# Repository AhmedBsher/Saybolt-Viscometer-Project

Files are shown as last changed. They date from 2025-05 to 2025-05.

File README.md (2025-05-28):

# Saybolt Viscometer Project

**Ahmed M. Bsher**<br>
ahmedbsher999@gmail.com<br>
**Alexandria University – Faculty of Engineering** – Mechanical Engineering

---

## Project Overview

This project is a Semi-Automated Saybolt Viscometer designed to measure the kinematic viscosity of Newtonian fluids. It combines mechanical design, sensor technology, microcontroller programming, and data analysis to provide a low-cost, modern alternative to traditional viscometers.

The viscometer measures the time taken for a fixed volume (60 ml) of fluid to flow through a standard orifice. This flow time is then used to calculate the fluid's viscosity using calibrated equations.

---

## Key Features

-   **Semi-Automated Measurement:** Uses an ESP32 microcontroller and an HC-SR04 ultrasonic sensor to automate fluid level measurement and time calculation.
-   **Real-Time Display:** LCD screen provides live viscosity readings.
-   **Dual Calibration:** Separate equations for fast-flowing and slow-flowing fluids to ensure accuracy.
-   **Python GUI Calculator:** A Tkinter-based application for easy viscosity calculation.
-   **Uncertainty Analysis:** Detailed MATLAB-based analysis to evaluate measurement accuracy and error sources.
-   **SolidWorks Design:** Precisely designed mechanical enclosure using SolidWorks23.

---

## Technologies and Tools Used

-   **ESP32 Microcontroller:** Main control unit for sensor data processing and output.
-   **HC-SR04 Ultrasonic Sensor:** For measuring fluid levels in the beaker.
-   **16x2 LCD Screen:** To display real-time viscosity readings.
-   **SolidWorks23:** For designing the mechanical enclosure.
-   **Python (Tkinter):** For developing the viscosity calculation GUI.
-   **MATLAB:** For uncertainty analysis.

---

## Project Components

### Mechanical Design

-   Designed in SolidWorks23 with a rectangular box enclosure, LCD screen cutout, and funnel opening.
-   Tab-and-slot construction for easy assembly and stability.
-   Internal support columns for the ultrasonic sensor.

### Sensor and Control System

-   HC-SR04 ultrasonic sensor for fluid level measurement.
-   ESP32 microcontroller for processing sensor data and displaying results.
-   16x2 LCD screen for displaying viscosity readings.

### Software

-   **ESP32 Firmware:** Code to read sensor data, calculate flow time, and display viscosity.
-   **Python GUI (`viscosity_calculation_gui.py`):**
    -   Tkinter application for viscosity calculation based on input time.
    -   Separate calibration equations for fast and slow flows.
-   **MATLAB Scripts:** For uncertainty analysis and error quantification.

---

## Calibration

-   Two sets of calibration equations:
    -   Fast-flowing fluids (water, milk): `v = 0.2447656223 * t - (0.06153034765 / t)`
    -   Slow-flowing fluids (oil): `v = 1.297738228 * t - (-235.6160549 / t)`
-   Calibration constants derived from tests with reference fluids.

---

## Uncertainty Analysis

-   Conducted using MATLAB to evaluate measurement accuracy.
-   Identified sources of uncertainty:
    -   Sensor resolution
    -   Wave reflection
    -   Power supply fluctuations
    -   Fluid properties
    -   Temperature errors
-   Calculated combined and expanded uncertainties to provide a confidence interval.

<p align="center">
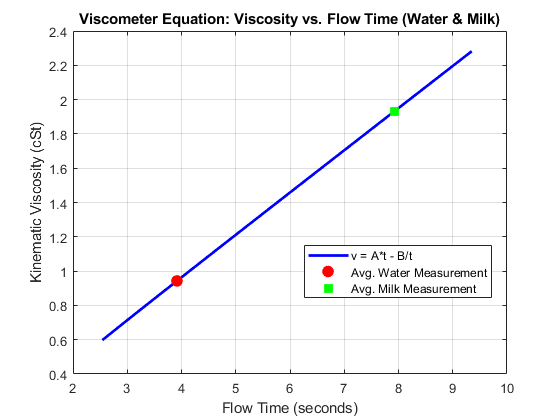
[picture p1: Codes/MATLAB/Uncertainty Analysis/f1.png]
  
</p>

<p align="center">
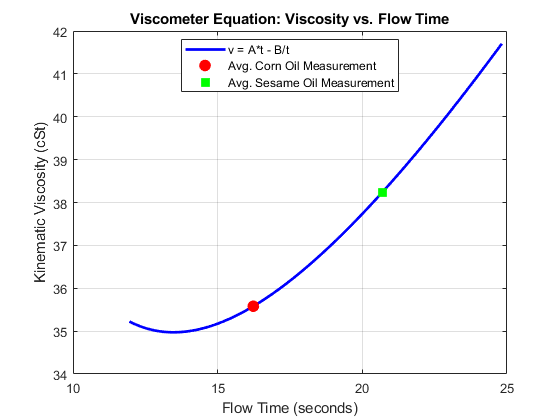
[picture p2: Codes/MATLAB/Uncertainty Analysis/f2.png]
  
</p>

---

## Getting Started

1.  Clone the repository to your local machine.
2.  Review the `SAYBOLT Viscometer Project Report.pdf` for detailed information.
3.  Explore the `Codes` folder for the Python GUI.
4.  Check the `Software` folder for the ESP32 firmware.
5.  Refer to the `Gallery` for project images.

### Running the Python GUI

1.  Ensure Python and Tkinter are installed.
2.  Navigate to the `Software` folder.
3.  Run `python viscosity_calculation_gui.py`.

---

## Contact

**Ahmed M. Bsher**<br>
ahmedbsher999@gmail.com<br>
[LinkedIn](https://www.linkedin.com/in/ahmed-bsher-921242232/)<br>
[Portfolio Website](https://ahmedbsher.github.io/My-Portfolio/)

---

## Tags

`#Engineering` `#Electronics` `#EmbeddedSystems` `#Viscosity` `#SayboltViscometer` `#ESP32` `#Arduino` `#Python` `#Tkinter` `#SolidWorks` `#Sensors` `#Measurement` `#FluidMechanics` `#Project`

---

## License

This project is licensed under the MIT License.

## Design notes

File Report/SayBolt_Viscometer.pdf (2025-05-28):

# Contents

3

# 1.Introduction:

Viscosity is one of the most important physical properties of fluids,

as it represents the internal resistance to flow. engineers must measure viscosity

Because it’s needed in many applications, such as lubrication systems, pipeline

design, chemical processing, and quality control. Our device is a classical

device that is used for determination of Newtonian fluids' kinematic viscosity

and its name Saybolt Viscometer

The working principle is simple measures the time it takes for a fixed volume

(typically 60 ml) of fluid to flow through a standard orifice at a specified

temperature

This project aims to simulate this process with a low-cost, Semi-automated

alternative using modern sensors and microcontrollers.

that provides live measurements and calculates viscosity with reasonable

accuracy.

The main objective is to design and construct an Semi-automated

## “Saybolt Viscometer”

4

# 2.Design and Methodology:

### 2.1 Mechanical Design

- Components
- Funnel
- Beaker
- Box
- 2 Wooden bars
- Box design

The outer box was designed with Solidworks23. A Rectangular cut-out

was included on the front panel for the LCD screen to allow clear

visibility of the readings. Additionally, an opening was made at the top to

securely insert the funnel used for fluid filling. The entire box was

assembled using a tab-and-slot construction method, ensuring ease of

assembly, precise alignment, and mechanical stability. Inside the box, the

ultrasonic sensor was fixed in place using two horizontal support

columns. These columns ensured that the sensor remained stable and

accurately aligned above the beaker for consistent distance

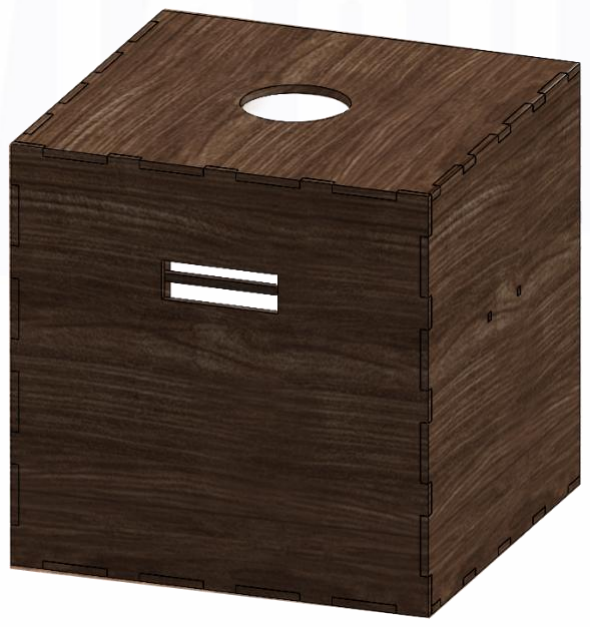
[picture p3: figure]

measurements.

5

### 2.2Sensor and Control System:

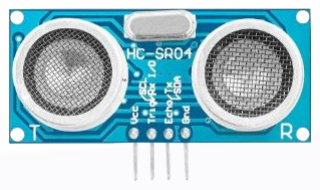
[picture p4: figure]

- HC-SR04 ultrasonic sensor

The sensor sits right atop the beaker
To measure the distance that is between the sensor and the rising
liquid level.
- ESP32 microcontroller

The ESP32 microcontroller is used as the main control unit in the Saybolt Viscometer project. It is responsible for receiving data from sensors, processing the information, and displaying the results.

- LCD

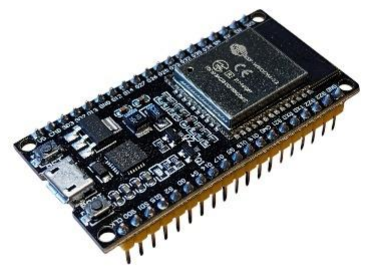
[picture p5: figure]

The screen is interfaced using multiple digital pins for direct control over each function (such as RS, EN, D4–D7), rather
than using a simplified I2C communication

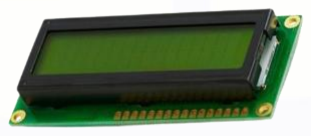
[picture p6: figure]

### 2.3 Operational Workflow

1. Fluid is poured into a funnel.

### 2. A beaker is placed under the funnel

### 3. Sensor measures the height of fluid

### 4. Height change is used to calculate time

### 5. Time for 60 ml to flow is calculated

### 6. Time is then used to calculate viscosity

6

## 3. Calibration:

Equation Format:

The standard empirical equation is:

## ν = A · t − (

B
t

)

Where :

- ν : Kinematic viscosity (mm²/s or cSt)
- t : Flow time in seconds
- A,B : Constants to be determined by calibration

We made two calibrated equations, one for fast-flowing fluids and the other for slow-flowing fluids

3.1: calibrating the equation for fast-flowing fluids

We used two equations for two different reference fluids to calculate the constants in Saybolt equation

1.Reference fluids:
1) Water:
properties:
- v water = 0.89 mm²
/s
- Volume used = 60 ml
- Measured discharge times (seconds): [3.32, 4.39, 3.32, 4.28, 3.21]
- Average time :
taveragefor water = (3.32 + 4.39 + 3.32 + 4.28 + 3.21) / 5 = 3.704 s
2) Milk:
properties:
- v milk = 1.8 mm²
/s
- Volume used = 60 ml
- Measured discharge times (seconds): [7.6, 7.39, 6.64, 7.49, 7.82]
- Average time :
taverge for milk =

7.6+7.39+6.64+7.49+7.82

5

= 7.388 s

7

2.Substituting into the Equation :

1) For water ∶ 0.89 = A ∗ 3.704 − (

B
3.704)
2) For milk ∶ 1.8 = A ∗ 7.388 – (

B
7.388)

∗ Solving the two equations and we get A, B ∗

A = 0.2447656223

B = 0.06153034765

3.Final calibrated equation for fast-flowing fluids :

v | = | 0.2447656223 | ∗ | t – | (

0.06153034765
t

)

3.2: calibrating the equation for slow-flowing fluids

We did the same process in oil.
1) Substituting into the Equation :
Solving the two equations and we get A,B

A = 1.297738228

B = −235.6160549

3.Final calibrated equation for slow-flowing fluids :

v | = | 1.297738228 | ∗ | t – (

−235.6160549
t

)

8

# 4. Testing and Results:

Results for Fast-Flowing Fluids

Fluid | Time (s) | Viscosity (mm²/s)
Water | 3.73 | 0.896
Water | 4.28 | 1.033
Water | 4.28 | 1.033
Water | 3.75 | 0.901
Water | 3.54 | 0.849
Milk | 8.35 | 2.036
Milk | 8.03 | 1.958
Milk | 7.7 | 1.877
Milk | 7.28 | 1.773
Milk | 8.24 | 2.009

Accuracy for water readings = 94.08 %

Accuracy for milk readings = 92.74 %

Results for Slow-Flowing Fluids

Fluid | Time (s) | Viscosity (mm²/s)
Oil | 13.95 | 34.993
Oil | 14.13 | 35.012
Oil | 18.94 | 37.019
Oil | 16.8 | 35.827
Oil | 17.34 | 36.091
Accuracy for Oil readings = 97.75 %

9

# 5.Uncertainty Analysis:

An uncertainty analysis was conducted to evaluate the accuracy of the viscosity measurements and identify potential sources of error.

### 5.1 Sources of Uncertainty

Several sources of uncertainty were identified based on the experimental setup and device characteristics:
- Sensor Resolution: The HC-SR04 sensor has a resolution of 0.3 cm, limited by the speed of sound and timing accuracy. Small changes in fluid level below this resolution may lead to unstable measurements. Additionally, variations in air density or humidity affect the speed of sound, introducing further errors.
- Wave Reflection: The fluid surface (e.g., oil or water) may reflect ultrasonic waves unevenly due to turbulence or transparency, weakening the signal and reducing measurement reliability, especially for highly reflective fluids.
- Power Supply: The ESP32 supplies the HC-SR04 with 5V via USB or another source. Voltage fluctuations can affect sensor performance, leading to inaccurate measurements.
- Viscometer Factors: Impurities or non-uniformity in the fluid composition may affect flow time, causing variability in viscosity measurements. Mechanical vibrations or instability in the setup can also impact sensor stability.
- Temperature Errors: Fluid temperature deviations cause a 1–2% error in viscosity per degree Celsius, while environmental temperature affects the HC-SR04 by approximately 0.17% per degree Celsius. This can result in a cumulative error of 2,5% in flow time if conditions are not controlled.

10

### 5.2 Uncertainty Calculation

### Theoretical Basis

- The kinematic viscosity (v) is calculated using the standard Saybolt Viscometer Equation, which describes the relationship between the flow time of a fluid through a calibrated orifice and its viscous properties:

## v = A ∗ t −

B
t
- A and B are the calibration constants specific to the viscometer used. For the purpose of this analysis, the uncertainty in these constants is assumed to be negligible.

1-Calculation of the Sensitivity Coefficient (dv/dt): This coefficient indicates how much the viscosity changes with a change in flow time. It's calculated by taking the derivative of the viscosity equation with respect to time:

2-Calculation of the Standard Uncertainty of the Mean Flow Time (ut ): This uncertainty is estimated from the observed variability in repeated flow time measurements. If we have n flow time measurements, the standard uncertainty of the mean time is calculated from the standard deviation

3-Assumption for Temperature Uncertainty (u_v _temperature)=0

4-Calculation of the Combined Standard Uncertainty (uc _(v)): To combine the individual uncertainty contributions from all relevant sources into a single overall value, the Law of Propagation of Uncertainty is applied.

dv
dt

= A +

B
T

2

Ut =

### std_dev(t)

√n

## uc _(v) = √(

dv
dt

∗ Ut)

## 2 + u_v _temperature²

11

## U = K ∗ uc _(v)

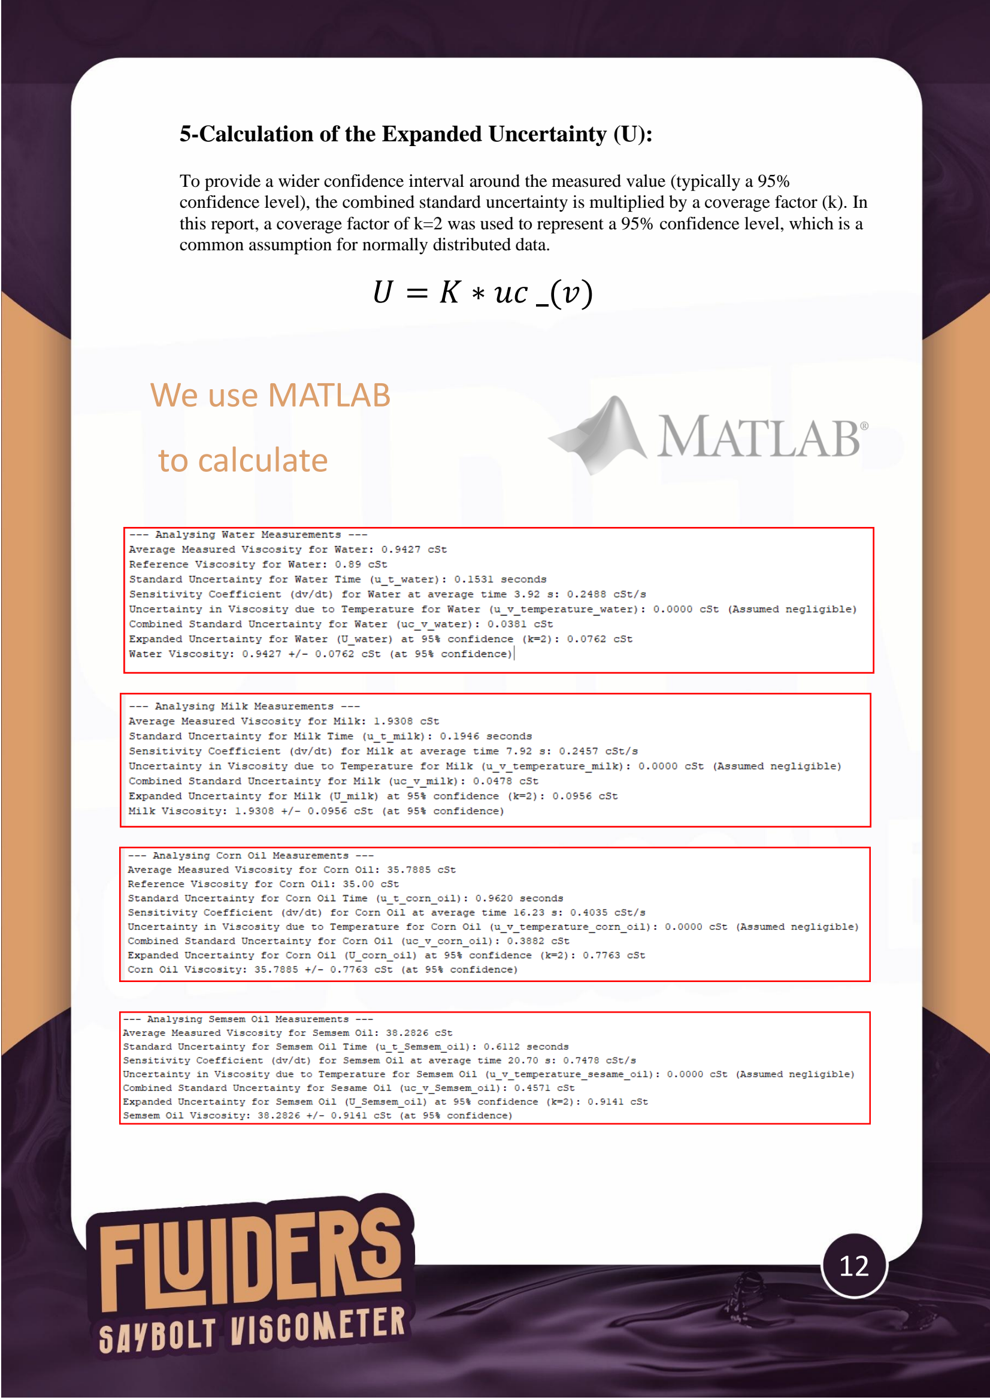
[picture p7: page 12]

5-Calculation of the Expanded Uncertainty (U):

To provide a wider confidence interval around the measured value (typically a 95% confidence level), the combined standard uncertainty is multiplied by a coverage factor (k). In this report, a coverage factor of k=2 was used to represent a 95% confidence level, which is a common assumption for normally distributed data.

# We use MATLAB

# to calculate

12

# 6.Discussion

6.1 Strengths of the Design:

- Low Cost: Utilizes affordable components accessible to students and hobbyists.
- Automation: The process is fully automated, eliminating the need for manual timing and control.
- Live Feedback: Real-time readings are displayed on the LCD screen, enhancing usability.
- Hands-On Learning: The project provided valuable experience in coding, circuit design, and hardware troubleshooting.
- Redesign Success: After an initial failure, we successfully created a functional design that fits all components properly.
6.2 Limitations:
- Ultrasonic Sensor Sensitivity: Highly affected by environmental noise, leading to unstable readings unless properly isolated.
- Initial Design Flaws: The first prototype did not accommodate the board and components effectively.
- Connection Issues: Wiring and circuit stability required extra effort and learning through trial and error.
- Lack of Temperature Control: Saybolt standards require 40°C or 100°C testing, while our setup operates at room temperature.
- Mathematical Complexity: Calculations required for viscosity were initially difficult to apply correctly.

6.3 Future Improvements:

- Replace ultrasonic sensor with a more stable alternative or apply digital signal filtering.
- Incorporate temperature sensors (e.g., DS18B20) to comply with Saybolt standard conditions.
- Modular Hardware Design: Easier troubleshooting and component swapping.
- Enhance coding structure for scalability and easier debugging.
- Add data logging capability via SD card or Bluetooth module for record keeping.

13

6.4 Cost:

- ESP : 320EGP
- HC-SR04 ultrasonic sensor : 45EGP
- Character LCD 16*2 Display Module : 70 EGP
- Jumpers : 45 EGP
- Design : 280 EGP
- Resistors : 5 EGP
- Metal Potentiometer : 5.50 EGP
- Breadboard : 40 EGP
- Cone : 25 EGP
- Beaker : 40 EGP
Total cost = 875.5 EGP

# 7.Conclusion

In conclusion, the Saybolt viscometer combined with an HC-SR04 ultrasonic sensor, ESP32 microcontroller introduces a novel low-cost digital method of measuring viscosity using digital accuracy for automatic data collection. Its accuracy is limited by uncertainties related to environmental influences on ultrasonic wave propagation, sensor resolution, microcontroller timing jitter, and fluid property or tube geometry variation. Using temperature compensation, careful calibration, stable power supplies, and sensor alignment, all these uncertainties can be reduced, making the system more reliable.

14

## 8. Project Gallery

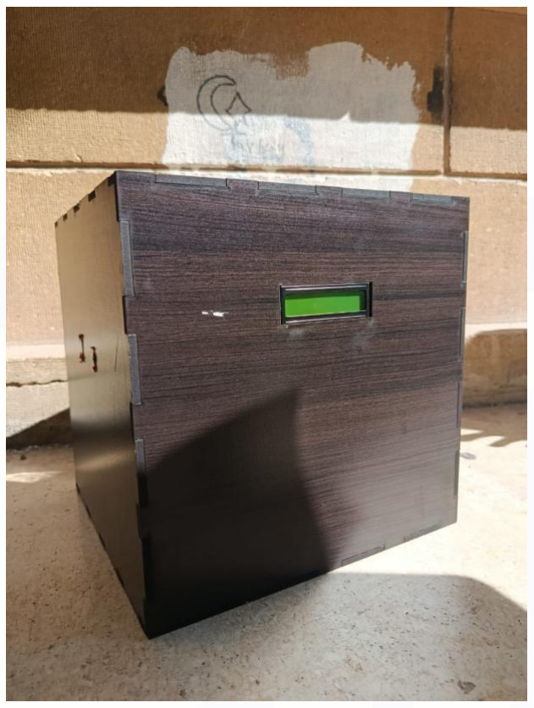
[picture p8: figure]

# 9. References:

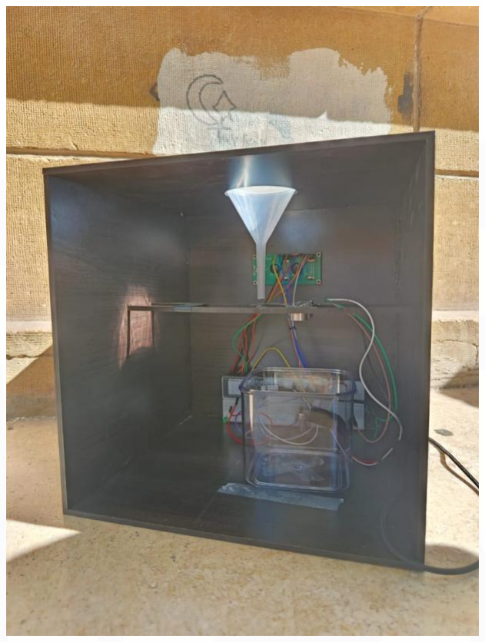
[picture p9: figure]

- https://instrumentationtools.com/saybolt-viscometer/
- https://www.slideshare.net/slideshow/saybolt-viscosity/125332774
- https://www.scribd.com/document/170513997/Say-Bolt-viscometer
- https://nvlpubs.nist.gov/nistpubs/nbstechnologic/nbstechnologicpaperT112e1.pdf
- ASTM International, Standard Test Method for Saybolt Viscosity, ASTM D88, 2018.Available: https://www.astm.org/d0088-18.html
- D. W. Green and M. Z. Southard, Perry’s Chemical Engineers’ Handbook, 9th ed. NewYork: McGraw-Hill Education, 2019, ch. 2.
- R. Santos and S. Araujo, “Using the HC-SR04 Ultrasonic Sensor with the ESP32,”Random Nerd Tutorials, 2021. [Online]. Available: https://randomnerdtutorials.com/esp32-hc-sr04-ultrasonic-arduino/
- Malarvizhi and R. Sudha, “Ultrasonic Measurement of Liquid Level,” International Journal of Engineering Research & Technology (IJERT), vol. 6, no. 8, pp. 1–4, Aug. 2017.
- A Beginner's Guide to Uncertainty of Measurement

15

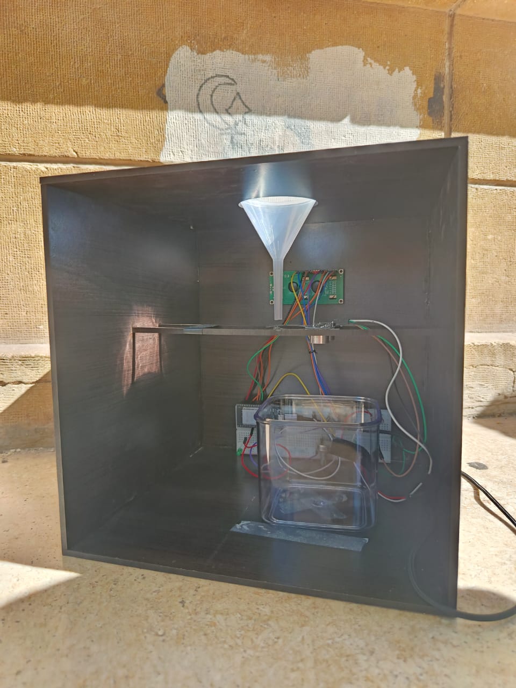
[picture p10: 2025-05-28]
Gallery/back.jpg

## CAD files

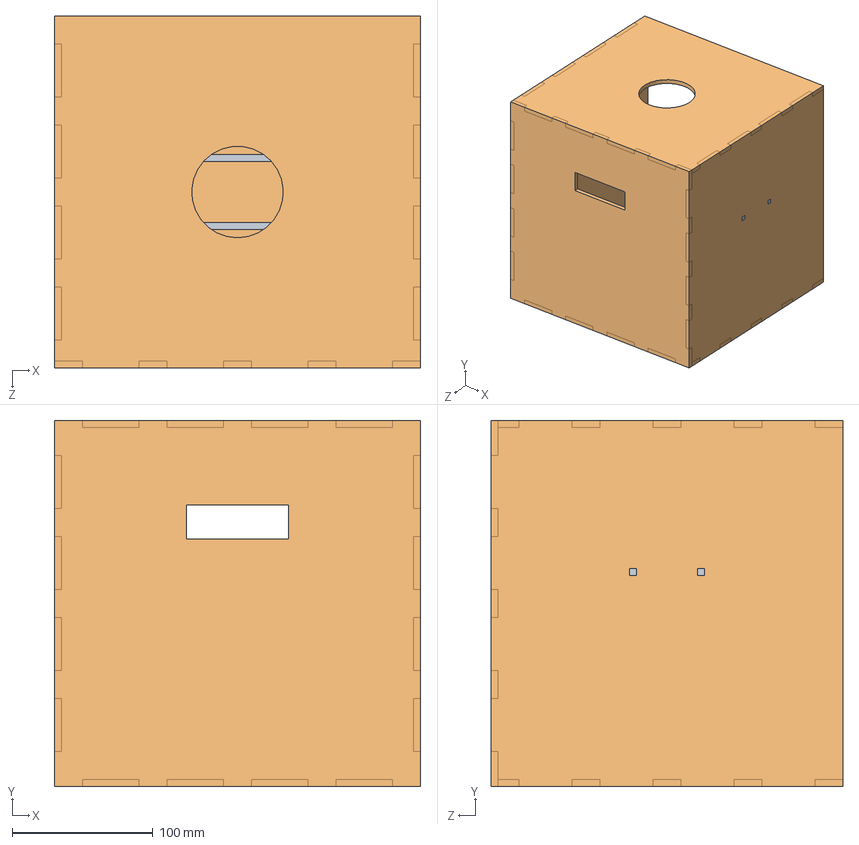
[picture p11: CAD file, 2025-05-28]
Design/Assem2.SLDASM
260.0 x 260.0 x 250.0 mm
arm x 2

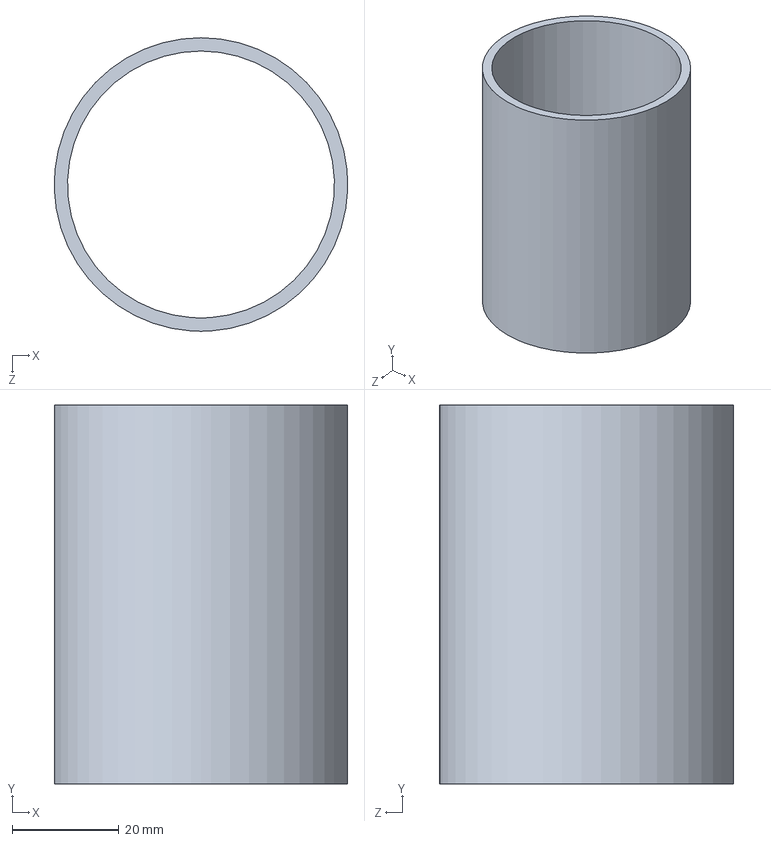
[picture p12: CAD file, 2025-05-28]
Design/baker.SLDPRT
55.0 x 71.0 x 55.0 mm

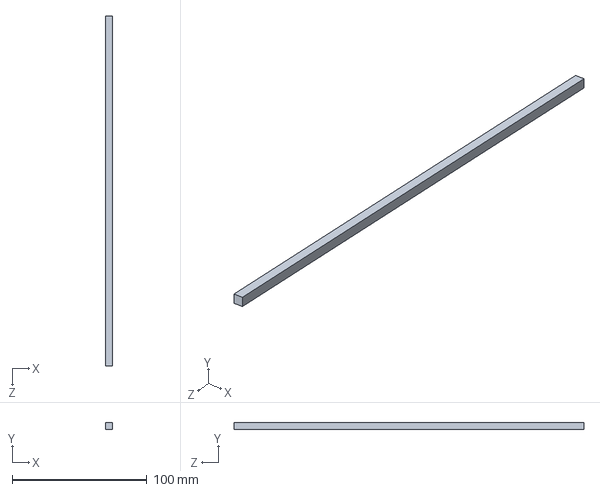
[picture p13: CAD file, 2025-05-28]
Design/arm.SLDPRT
5.00 x 5.00 x 260.0 mm

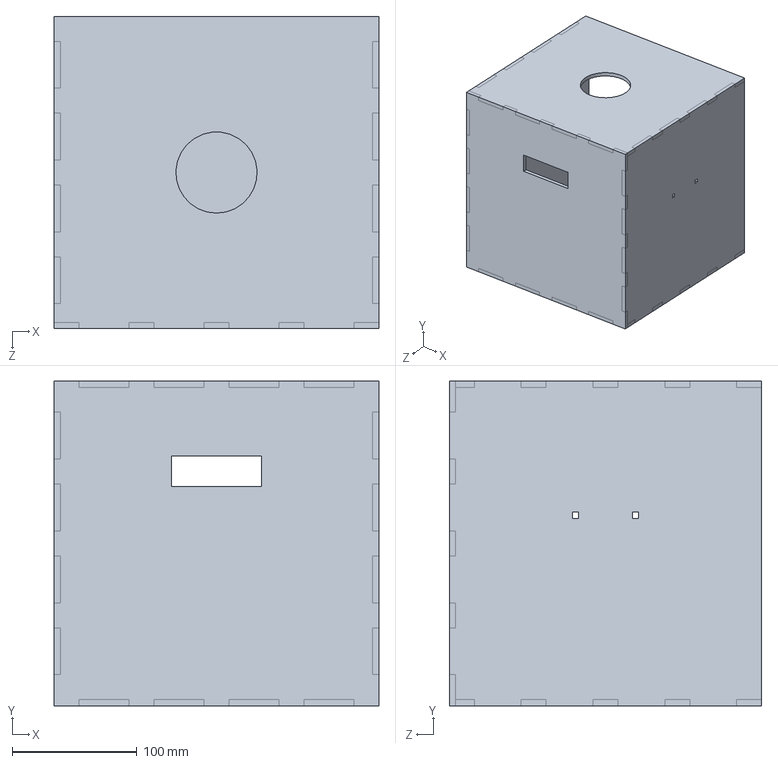
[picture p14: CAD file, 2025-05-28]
Design/box.SLDPRT
260.0 x 260.0 x 250.0 mm

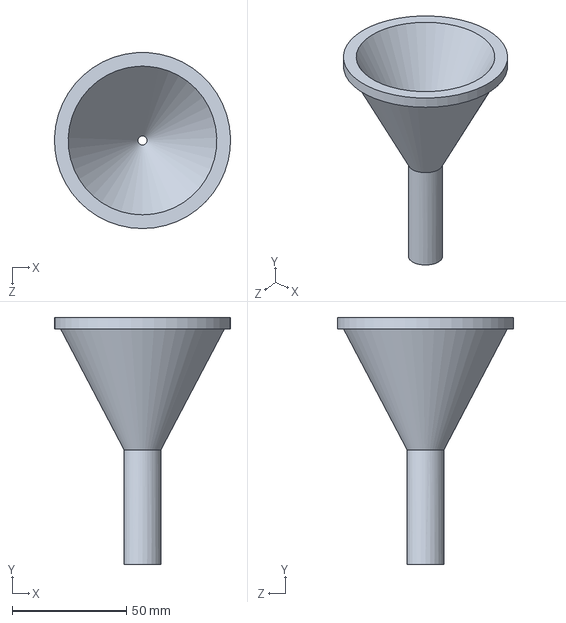
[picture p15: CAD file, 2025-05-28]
Design/cone.SLDPRT
77.0 x 108.0 x 77.0 mm

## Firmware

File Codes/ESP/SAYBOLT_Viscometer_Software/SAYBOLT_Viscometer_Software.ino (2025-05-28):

#include <LiquidCrystal.h>

// LCD pins: RS, E, D4, D5, D6, D7
LiquidCrystal lcd(21, 22, 18, 19, 23, 5);

// Ultrasonic sensor pins
#define TRIG_PIN 4
#define ECHO_PIN 16
#define LED_PIN 32

// Measurement parameters
const float SOUND_SPEED = 0.034; // cm/μs
const float MIN_DISTANCE = 10.00;  // cm
const float MAX_DISTANCE = 15.00;  // cm

#define MEDIAN_FILTER_SIZE 5
float distanceBuffer[MEDIAN_FILTER_SIZE];
byte bufferIndex = 0;
const float SMOOTHING_FACTOR = 0.7;
float smoothedDistance = 0;
float lastValidDistance = 0;

const int DEBOUNCE_COUNT = 3;
int debounceCounter = 0;
unsigned long startTime = 0;
unsigned long stopTime = 0;
bool timing = false;
bool finished = false;
bool gracePeriod = true;
unsigned long graceStartTime = 0;
const unsigned long GRACE_PERIOD = 10000;

const float D1 = 13.84;
const float D2 = 11.835;

const float A_FAST = 0.2447656223;
const float B_FAST = 0.06153034765;
const float A_SLOW = 1.297738228;
const float B_SLOW = -235.6160549;
const float TIME_THRESHOLD = 10.0;

void setup() {
  Serial.begin(115200);
  pinMode(TRIG_PIN, OUTPUT);
  pinMode(ECHO_PIN, INPUT);
  pinMode(LED_PIN, OUTPUT);

  lcd.begin(16, 2);
  lcd.print("Initializing...");

  for (byte i = 0; i < MEDIAN_FILTER_SIZE; i++) {
    distanceBuffer[i] = getRawDistance();
    delay(50);
  }

  lastValidDistance = medianOfArray(distanceBuffer, MEDIAN_FILTER_SIZE);
  smoothedDistance = lastValidDistance;

  graceStartTime = millis();
  updateDisplay();
  Serial.println("System Ready - Enhanced Stability Active");
}

void loop() {
  if (finished) {
    delay(1000);
    return;
  }

  float currentDistance = getFilteredDistance();
  updateDisplay();

  Serial.print("Filtered: ");
  Serial.print(currentDistance, 2);
  Serial.print("cm | Grace: ");
  Serial.println(gracePeriod ? "Yes" : "No");

  if (gracePeriod && (millis() - graceStartTime > GRACE_PERIOD)) {
    gracePeriod = false;
    lcd.setCursor(0, 1);
    lcd.print("Ready to measure ");
    Serial.println("Grace Period Ended");
  }

  if (!gracePeriod && !timing) {
    checkMeasurementStart(currentDistance);
  }

  if (timing && currentDistance < D2) {
    stopMeasurement();
  }

  delay(100);
}

void checkMeasurementStart(float currentDistance) {
  if (currentDistance < D1 && currentDistance > D2) {
    debounceCounter++;
    if (debounceCounter >= DEBOUNCE_COUNT) {
      startTime = millis();
      timing = true;
      digitalWrite(LED_PIN, HIGH);
      lcd.setCursor(0, 1);
      lcd.print("Measuring...    ");
      Serial.println("Measurement Started - Valid Trigger");
      debounceCounter = 0;
    }
  } else {
    debounceCounter = 0;
  }
}

void stopMeasurement() {
  stopTime = millis();
  float seconds = (stopTime - startTime) / 1000.0;

  float viscosity;
  if (seconds < TIME_THRESHOLD) {
    viscosity = A_FAST * seconds - B_FAST / seconds;
    Serial.print("Used fast flow constants | ");
  } else {
    viscosity = A_SLOW * seconds - B_SLOW / seconds;
    Serial.print("Used slow flow constants | ");
  }

  showFinalResults(seconds, viscosity);
  digitalWrite(LED_PIN, LOW);
  finished = true;
}



float getRawDistance() {
  digitalWrite(TRIG_PIN, LOW);
  delayMicroseconds(2);
  digitalWrite(TRIG_PIN, HIGH);
  delayMicroseconds(10);
  digitalWrite(TRIG_PIN, LOW);

  long duration = pulseIn(ECHO_PIN, HIGH, 30000); // Timeout added
  float distance = duration * SOUND_SPEED / 2;

  if (distance < MIN_DISTANCE || distance > MAX_DISTANCE || duration == 0) {
    return lastValidDistance;
  }

  return distance;
}

float medianOfArray(float arr[], byte size) {
  float sorted[size];
  memcpy(sorted, arr, size * sizeof(float));

  for (byte i = 0; i < size - 1; i++) {
    for (byte j = i + 1; j < size; j++) {
      if (sorted[j] < sorted[i]) {
        float temp = sorted[i];
        sorted[i] = sorted[j];
        sorted[j] = temp;
      }
    }
  }

  if (size % 2 == 0) {
    return (sorted[size/2 - 1] + sorted[size/2]) / 2;
  } else {
    return sorted[size/2];
  }
}

float getFilteredDistance() {
  float newReading = getRawDistance();

  distanceBuffer[bufferIndex] = newReading;
  bufferIndex = (bufferIndex + 1) % MEDIAN_FILTER_SIZE;

  float median = medianOfArray(distanceBuffer, MEDIAN_FILTER_SIZE);
  smoothedDistance = SMOOTHING_FACTOR * median + (1.0 - SMOOTHING_FACTOR) * smoothedDistance;

  lastValidDistance = smoothedDistance;
  return smoothedDistance;
}

void updateDisplay() {
  lcd.setCursor(0, 0);
  lcd.print("Dist: ");
  lcd.print(smoothedDistance, 1);
  lcd.print(" cm    ");
}

void showFinalResults(float seconds, float viscosity) {
  lcd.clear();
  lcd.setCursor(0, 0);
  lcd.print("Time: ");
  lcd.print(seconds, 2);
  lcd.print("s");

  lcd.setCursor(0, 1);
  lcd.print("Visc: ");
  lcd.print(viscosity, 2);
  lcd.print(" cSt");

  Serial.print("Time: ");
  Serial.print(seconds, 2);
  Serial.print("s | Viscosity: ");
  Serial.print(viscosity, 2);
  Serial.println(" cSt");
}
